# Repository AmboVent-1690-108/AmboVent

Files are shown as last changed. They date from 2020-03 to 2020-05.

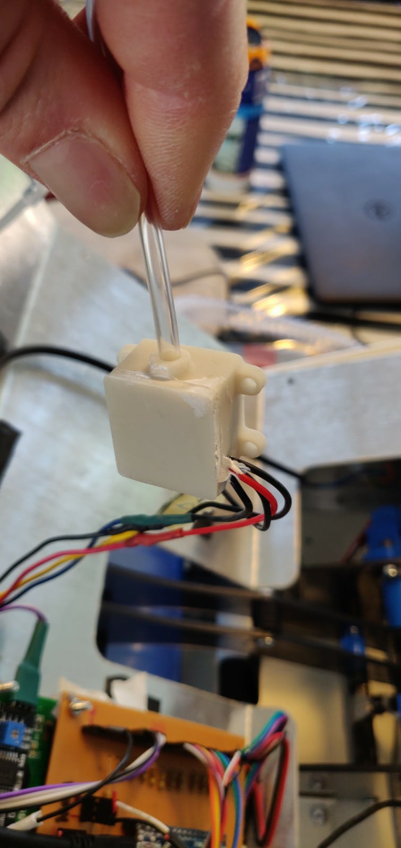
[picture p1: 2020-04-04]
Pressure Sensor/Pictures/WhatsApp Image 2020-04-04 at 16.27.53 (1).jpeg

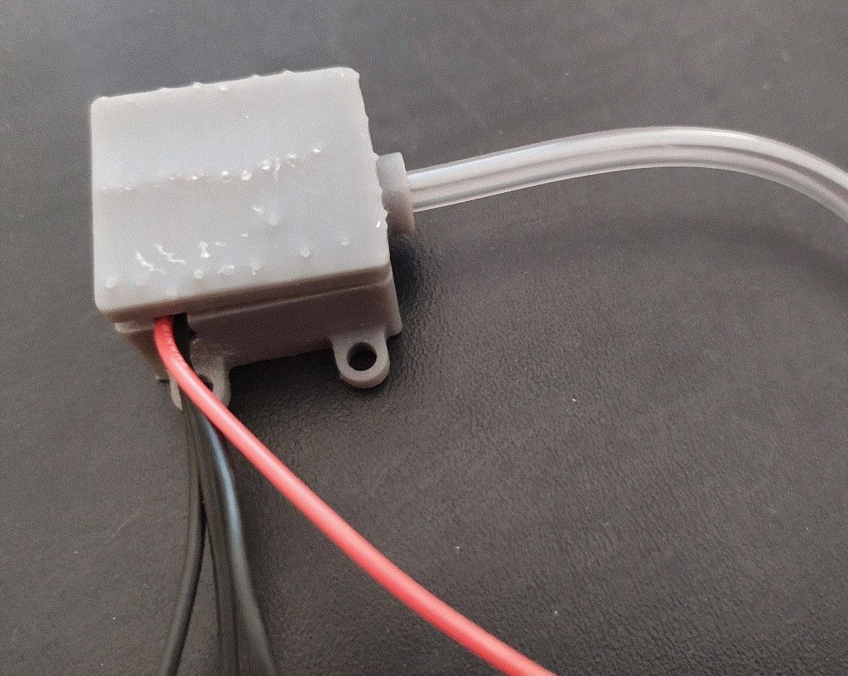
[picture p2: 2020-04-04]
Pressure Sensor/Pictures/WhatsApp Image 2020-04-04 at 16.28.07.jpeg

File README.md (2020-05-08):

# AmboVent  1690.108

    Automatic, Controlled Resuscitator Device
    Emergency ventilation alternative system
    Global Partnership for the Greater good
    Leading Open Source Code Mentality Initiative

## Emergency ventilation initiative coming out of Israel

## The device was not tested yet for its performance or safety; it is NOT approved for clinical use

### Who is behind it?  
**Lead by the CTO & innovation leader of the Israeli Air-Force 108 Electronic Depot and backed by a large community of innovators behind him, to include:**

1. 40 Professional Volunteers
1. Magen David Adom (Israel’s national EMS)
1. Physicians from leading Israeli hospitals such as Tel Aviv Sourasky and Hadassah JLM as well as other medical centers, Engineers, FIRST Israel mentors and students
1. The Haifa Technological Center Rafael
1. Israel Aerospace Industries
1. IAF Unit 108
1. The garage program by Microsoft Israel
1. IDC Herzeliya
1. and others...

## Developer Chat on Gitter:



## [AmboVent Website](https://1nn0v8ter.rocks/AmboVent-1690-108)

## [BOM list](https://docs.google.com/spreadsheets/d/1yqxRhruZpR-hO4cpbX6UkSeXTlXk1JLd_4aYDwuWj4k/edit?usp=sharing)

# AmboVent's Standard Copyright and Disclaimer Notice:

*Copyright ©2020. THE AMBOVENT GROUP FROM ISRAEL herby declares:  No Rights Reserved. Anyone in the world have Permission to use, copy, modify, and distribute this software and its documentation for educational, research, for profit, business and not-for-profit purposes, without fee and without a signed licensing agreement, all is hereby granted, provided that the intention of the user is to use this code and documentation to save human lives  anywhere in the world. For any question, contact dreliram@gmail.com.*

***IN NO EVENT SHALL THE AMBOVENT GROUP FROM ISRAEL, BE LIABLE TO ANY PARTY FOR DIRECT, INDIRECT, SPECIAL, INCIDENTAL, OR CONSEQUENTIAL DAMAGES, INCLUDING LOST PROFITS, ARISING OUT OF THE USE OF THESE SPECS, LIST OF MATERIALS, ELECTRONIC DESIGNS , SOFTWARE CODE AND ANY DOCUMENTATION, EVEN IF THE AMBOVENT GROUP FROM ISRAEL HAS BEEN ADVISED OF THE POSSIBILITY OF SUCH DAMAGE.
THE AMBOVENT GROUP FROM ISRAEL DISCLAIMS ANY WARRANTIES, INCLUDING, BUT NOT LIMITED TO, THE IMPLIED WARRANTIES OF MERCHANTABILITY AND FITNESS FOR A PARTICULAR PURPOSE. THE SOFTWARE AND ACCOMPANYING DOCUMENTATION, SPECS, LIST OF MATERIALS, ELECTRONIC DESIGNS, SOFTWARE CODE AND ANY DOCUMENTATION IF PROVIDED HEREUNDER IS PROVIDED "AS IS". THE AMBOVENT GROUP FROM ISRAEL HAS NO CLAIM THAT IT IS COMPLETED OR FUNCTIONAL AND HAS NO OBLIGATION TO PROVIDE MAINTENANCE, SUPPORT, UPDATES, ENHANCEMENTS, OR MODIFICATIONS.***

# Setup

## Software

1. (Required to build the code): [Arduino IDE](https://www.arduino.cc/en/Main/Software)
1. (Optional: recommended to edit the code): Eclipse project for Arduino source code _editing_ (NOT building):
    1. A general setup PDF guide can be found in the [eRCaGuy_dotfiles](https://github.com/ElectricRCAircraftGuy/eRCaGuy_dotfiles) project [here](https://github.com/ElectricRCAircraftGuy/eRCaGuy_dotfiles/blob/master/eclipse/Eclipse%20setup%20instructions%20on%20a%20new%20Linux%20(or%20other%20OS)%20computer.pdf). See also:
    1. [3-Software/Arduino/readme.md](3-Software/Arduino/readme.md).
    1. [3-Software/Arduino/arduino_core/readme.md](3-Software/Arduino/arduino_core/readme.md)
    1. [3-Software/Arduino/.clang-format](3-Software/Arduino/.clang-format) - there are some nice descriptions & info in here on Eclipse & Sublime Text 3 editors, as well as setting your Arduino IDE to use 4 spaces instead of 2 for tabs.
1. (Required to get a pull request accepted which modifies the code): `clang-format` automatic code format tool. Please run this on any PR (GitHub Pull Request) before submitting a PR!
    1. Linux (tested--works): 
        1. Install: 

                # Install it:
                sudo apt update
                sudo apt install clang-format

                # Ensure you have version 6 (the default for Ubuntu 18), for compatibility with 
                # the .clang-format file we are using; sample output: 
                # `clang-format version 6.0.0-1ubuntu2 (tags/RELEASE_600/final)`
                clang-format --version
        
        1. Use it: 
            1. Commit your changes so everything is backed up.
            1. Then run the clang formatter:

                    ./run_clang-format.sh

            1. Then review and commit these changes, if any.
            1. Now do a Pull Request.

    1. Windows:
        1. Install:
            1. Download and install [Git for Windows](https://git-scm.com/download/win)
            1. Download and install LLVM (which includes `clang-format`) version **6.0.1** (for compatibility--see above) [for Windows, here](https://releases.llvm.org/download.html). Here's a [direct link](https://releases.llvm.org/6.0.1/LLVM-6.0.1-win64.exe) if you like for the 64-bit version.
        1. Use it:
            1. Using the git bash terminal that comes with git for Windows, run the script:

                    ./run_clang-format.sh

            1. Make sure to do this before making any Pull Request (see Linux "Use it" instructions just above as well).

# Software Changelog
- Newest on top
- Follows Semantic Versioning: MAJOR.MINOR.PATCH; see: https://semver.org/ for rules & FAQ.
- The 6 most common recommended types of changes are (see here: https://keepachangelog.com/en/1.0.0/): Added, Changed, Deprecated, Removed, Fixed, Security

INITIAL DEVELOPMENT PHASE:
- Use version numbers 0.MINOR.PATCH for the initial development phase; ex: 0.1.0, 0.2.0, etc.
- Increment just the MINOR version number for each new 0.y.z development phase enhancement, until the project is mature enough that you choose to move to a 1.0.0 release
- You may increment the PATCH number for bug fixes to your development code, or just increment the MINOR version number if there are also enhancements

MORE MATURE PHASE:
- As the project matures, release a 1.0.0 version
- Once you release a 1.0.0 version, do the following (copied from semver.org):
- Given a version number MAJOR.MINOR.PATCH, increment the:  
1. MAJOR version when you make incompatible API changes,  
2. MINOR version when you add functionality in a backwards compatible manner, and  
3. PATCH version when you make backwards compatible bug fixes.  

## [v0.1.0] - 2020-04-22
- Added: changelog and started tracking a software "version" number via the changelog
- Fixed: continued incremental improvements of the software formatting and style: ex: moved global variables to their own lines

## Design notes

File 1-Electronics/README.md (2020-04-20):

AmboVent Electronic Design
--------------------------
## This directory contains the files needed to produce and/or change the electronic control board of AmboVent.

### The controller consist of a single PCB, with Arduino Nano mounted on it and a few other components. The board contains header connectors for varios system components:
- Front panel controls (pushbuttons, potentiometers, LEDs)
- Power input
- PWM control to the main motor
- Arm location feedback (potentiometer)
- I2C pressure sensor
 
All connectors have 0.1" spacing, and can accept either male or female headers. The power
input connector has 5mm spacing and it is designed for screw terminal connector type, but
direct wire connection is also feasible.

The PCB is designed with single layer, quick CNC fabrication in mind. It can be milled
with 1/32 mill. In this case, assembly will require a few wire bridges. If traditional, 
two layer fabrication method is used, a top layer can be used in place of the wire bridges.

#### SW1 – D2 - test button (used to initiate calibration)
#### SW2 – D4 - toggle breath on/off
#### SW3 – D5 - reset alarm button
#### Pot 1 – A2 – sets the range of motion as percentage from full range as set in calibration
#### Pot 2 – A3 – sets the respiration rate from 6 to 24 per minute
#### Pot 3 – A6 – sets the inspirium pressure from 30 to 70 cm H2O
#### J3 – connects to the position sensor potentiometer in the arm
#### J4 – connects to the motor controller PWM input (usually don’t connect the 5V)
#### J5 – connector to pressure sensor – if you use a 3.3V pressure sensor – supply 3.3V from the Arduino instead of the 5V

**Assemble the potentiometer for arm position sense such that when the arm moves down (presses the
Ambu more) – the voltage goes up. Range 0-5 volts
Assemble the user interface potentiometers such that during clockwise motion the voltage goes up.
Range 0-5 volts
Motor polarity shall be set such that PWM>50% to the controller results in the arm pressing the Ambu
(moving down).
The SW calibration procedure enable easy verification of the motor and position feedback polarity
(see calibration video for details)**

_Please note that the current sensor is **NOT** needed if you are using pressure sensor, it's possible to use it to monitor and limit the motor current while using the pressure sensor but again, not mandatory._

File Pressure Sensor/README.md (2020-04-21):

## General comments on the pressure sensor

_Please note that this sensor requires VDD of 3.3V and pull up to signal on the **SAME** VDD input, so using the current board schem could **damage** the sensor_

# Presure sensor and board
---------------------------------

We used the "SparkFun Pressure Sensor Breakout - MS5803-14BA"
The item can be found at the following link for $60US:
https://www.sparkfun.com/products/12909
It also can be found at other suppliers usually for the same price.

It is based of the TE MS5803-14BA sensor which can be bought
separately for cheaper price but usually in quantities of hundreds.
https://www.futureelectronics.com/p/analog--sensors--pressure/ms580314ba01-00-te-sensor-solutions-5058846
https://www.mouser.com/ProductDetail/Measurement-Specialties/MS580314BA01-00?qs=sGAEpiMZZMueJGT%2F0PGc4wvItXGMkWfD%252B0JwHIbyHlk%3D
If one uses the basic TE sensor a board should be designed with
few capacitors and resistors.

In case one want to use a different pressure sensor, we
recommend the following:
1. Pressure range is 100mbar (100cm H2O)
2. Digital communication - I2C preferred (analog communication 
will require high frequency averaging)

In case one prefer to use differential pressure sensor it will
improve reliability but will require a slightly change in the
arduino code.

Presure sensor box
---------------------------------

The box and cover are made from liquid ABS, using SLA technology
with resolution 0.05 to allow sealed box.

It is recommended to use flexible silicone wires to reduce stress
when mounting the pressure sensor in the box. 

Use a sealing silicone on the wires and around the box cover to
ensure complete sealed box

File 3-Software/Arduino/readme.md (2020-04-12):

## Description of files & folders:

## Main folders:
1. arduino_core = contains a symbolic link called "arduino" to the arduino installation directory so that your Eclipse project, for instance, can index it and allow you to jump to it while exploring the code
2. Libraries = required Arduino libraries you need to build this project
3. ventilation_machine = the main source code for this project

## Other files & folders:
1. .settings = Eclipse folder for this project
2. .cproject = Eclipse project file
3. .project = Eclipse project file
4. readme.md = this file

**Note that if you're new to Eclipse, a general setup PDF guide can be found in the [eRCaGuy_dotfiles](https://github.com/ElectricRCAircraftGuy/eRCaGuy_dotfiles) project [here](https://github.com/ElectricRCAircraftGuy/eRCaGuy_dotfiles/blob/master/eclipse/Eclipse%20setup%20instructions%20on%20a%20new%20Linux%20(or%20other%20OS)%20computer.pdf).**

When setting up an Eclipse project for Arduino, just set it up as a C/C++ project, then tell Eclipse that `*.ino` files are a type of C++ Source File (so that it will index them and open them up in its C/C++ editor with proper syntax highlighting) by following these instructions here: https://stackoverflow.com/questions/33474629/is-ecplise-cdts-indexer-limited-to-the-common-filetypes-for-sources-and-headers/33520998#33520998. In short: Window --> Preferences --> C/C++ --> File Types --> click "New..." --> type in "*.ino" as the pattern, and set the "Type" to "C++ Source File" --> click "OK" --> "Apply and Close". Eclipse will now automatically re-index the whole project, indexing all *.ino files as C++ source files! *These instructions have now been added to my Eclipse PDF doc above!*

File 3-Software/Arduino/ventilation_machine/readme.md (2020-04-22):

## Build size notes:
(Newest on TOP; date format is YYYYMMDD)

---

20200422-0136hrs (git hash 222e6966211a877936bd2962692c0c57bd665e2f; branch more_incremental_improvements) (IDE 1.8.12) (Arduino Nano)  
Note: memory usage went up because we are now storing and printing the version number at startup.

    Sketch uses 18318 bytes (56%) of program storage space. Maximum is 32256 bytes.
    Global variables use 1074 bytes (52%) of dynamic memory, leaving 974 bytes for local variables. Maximum is 2048 bytes.

---

20200420-0049hrs (git hash 493985f; branch fix_formatting) (IDE 1.8.12) (Arduino Nano) - PR #46: https://github.com/AmboVent-1690-108/AmboVent/pull/46

    Sketch uses 18176 bytes (56%) of program storage space. Maximum is 32256 bytes.
    Global variables use 1046 bytes (51%) of dynamic memory, leaving 1002 bytes for local variables. Maximum is 2048 bytes.

---

20200419-2312hrs (git hash 078871e05ddd5890747f49222d46a7b30fd7b023; branch master) (IDE 1.8.12) (Arduino Nano) - no changes made yet to the code:

    Sketch uses 18174 bytes (56%) of program storage space. Maximum is 32256 bytes.
    Global variables use 1046 bytes (51%) of dynamic memory, leaving 1002 bytes for local variables. Maximum is 2048 bytes.

---

20200411-2217hrs (IDE 1.8.8) (Arduino Nano) - no changes made yet to the code:

    Sketch uses 18280 bytes (59%) of program storage space. Maximum is 30720 bytes.
    Global variables use 1882 bytes (91%) of dynamic memory, leaving 166 bytes for local variables. Maximum is 2048 bytes.
    Low memory available, stability problems may occur.

---

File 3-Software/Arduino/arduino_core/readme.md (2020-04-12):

Inside this folder should be a symbolic link to your arduino installation folder. This way, an Eclipse project, for instance, can have full access to all of the Arduino source code to allow jumping to the core implementations of Arduino functions and definitions while exploring the code. 

## References:
1. How to make symbolic links in Windows: 
   https://www.howtogeek.com/howto/16226/complete-guide-to-symbolic-links-symlinks-on-windows-or-linux/

## How to make the symbolic link to the core Arduino source code:

**1) To create a symbolic link on Mac or Linux**, the command looks like this. This will create a symbolic link folder called "arduino" right here: 

    ln -s "/path/to/arduino_installation_folder" arduino

Example: 

    cd /path/to/here
    ln -s "/home/gabriel/Downloads/Install_files/Arduino/arduino-1.8.8" arduino

**2) To create a symbolic link on Windows**, the command looks like this:

    mklink /D arduino "C:\Users\gabriel\Downloads\Install_files\Arduino\arduino-1.8.8"

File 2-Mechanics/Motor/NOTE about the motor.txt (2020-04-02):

We used the am-2235a Snow Blower Motor With Hex Shaft

Any equivalent motor can fit, with a relevant adapter.
- 12V
- RPM 70 to 100
- Torque >7NM

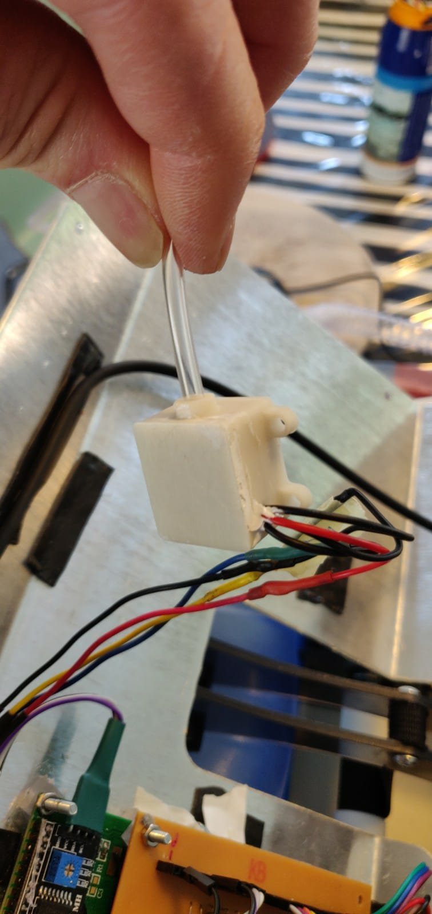
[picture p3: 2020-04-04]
Pressure Sensor/Pictures/WhatsApp Image 2020-04-04 at 16.27.52 - Copy.jpeg

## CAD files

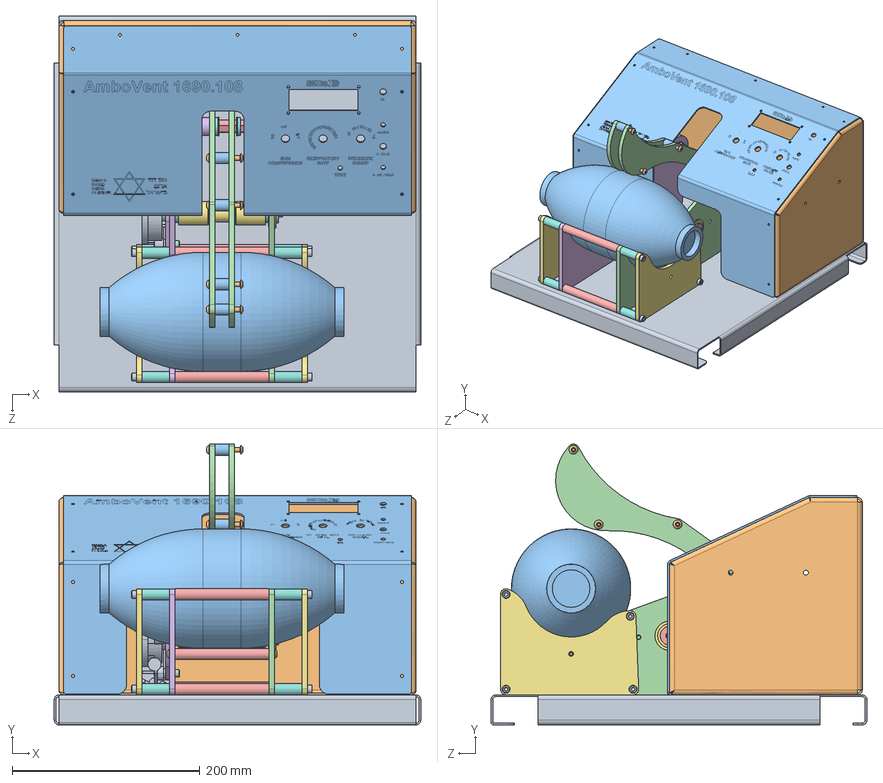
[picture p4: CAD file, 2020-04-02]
2-Mechanics/Casing/AMBOVENT.SLDASM
390.0 x 298.8 x 400.0 mm
AMBOVENT-1-1
AMBOVENT-1-2
AMBOVENT-1-3-1
socket head cap screw_am x 10
socket button head cap screw_am x 14
0.5in Hex 1.125in OD 217-3875 Flanged Bearing x 3
E-clip 0.5in shaft x 2
Ambu Air Tank
EMS22Q51-B28-LS4 Digikey EMS22Q51-B28-LS4-ND
am-2235a SnowBlower with Hex Shaft
socket head cap screw_ai x 4
flat washer wide_am
prevailing torque hex nut_am x 2

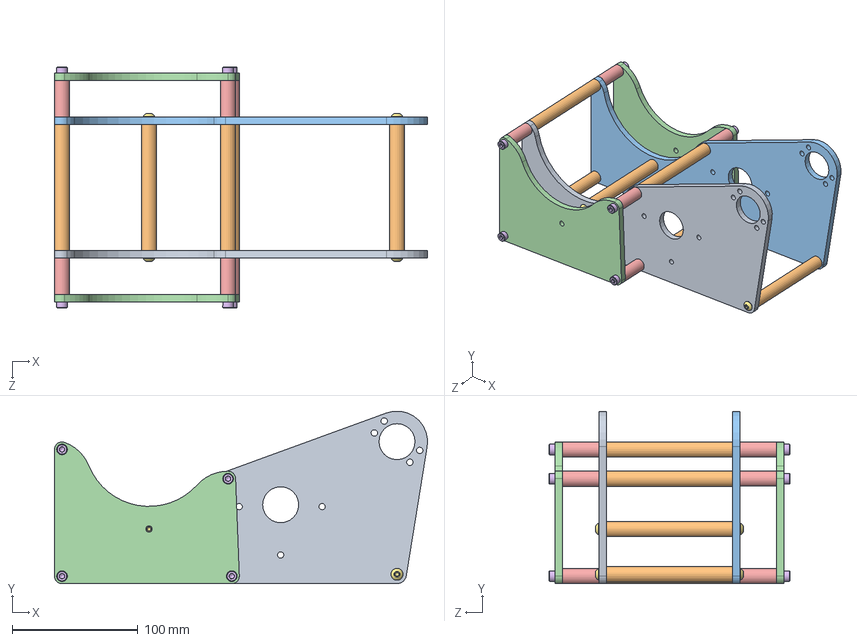
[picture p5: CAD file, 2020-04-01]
2-Mechanics/Mechanism/SolidWorks Pack and Go/1690-20-8320.SLDASM
296.9 x 137.2 x 192.0 mm
socket head cap screw_am x 8
socket button head cap screw_am x 4

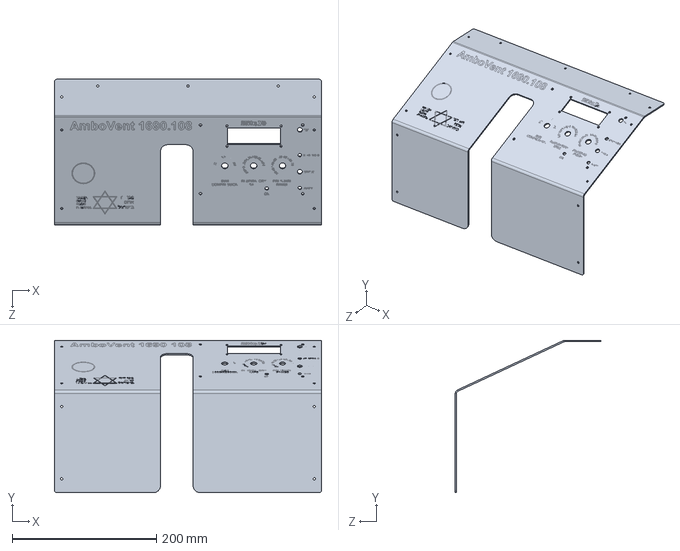
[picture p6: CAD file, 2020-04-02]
2-Mechanics/Casing/AMBOVENT-1-3.SLDASM
370.0 x 211.2 x 201.7 mm

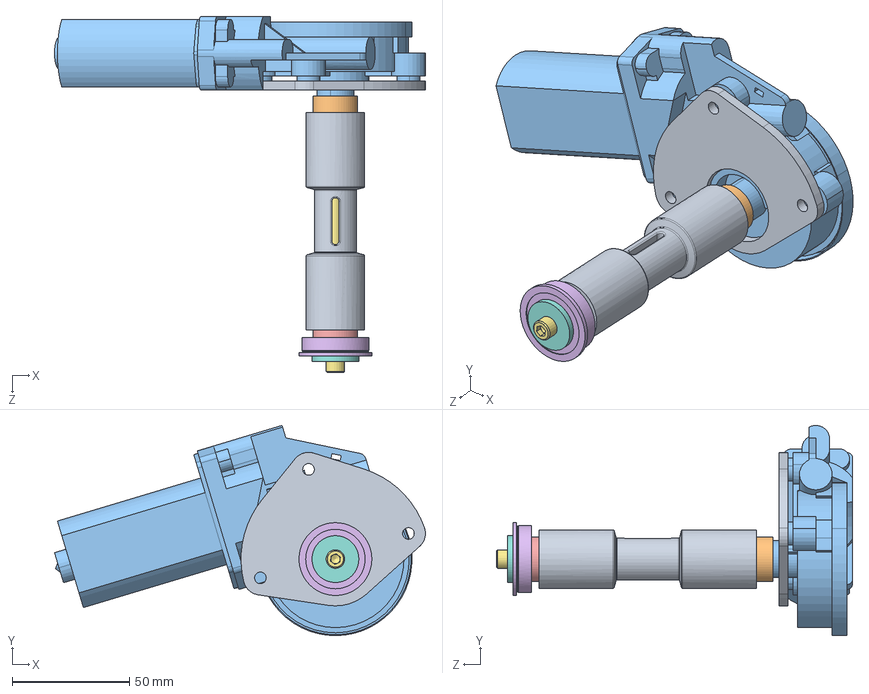
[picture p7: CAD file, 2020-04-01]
2-Mechanics/Mechanism/SolidWorks Pack and Go/1690-20-8390.SLDASM
158.5 x 89.8 x 152.2 mm
am-2235a SnowBlower with Hex Shaft
0.5in Hex 1.125in OD 217-3875 Flanged Bearing
socket head cap screw_ai
flat washer wide_am

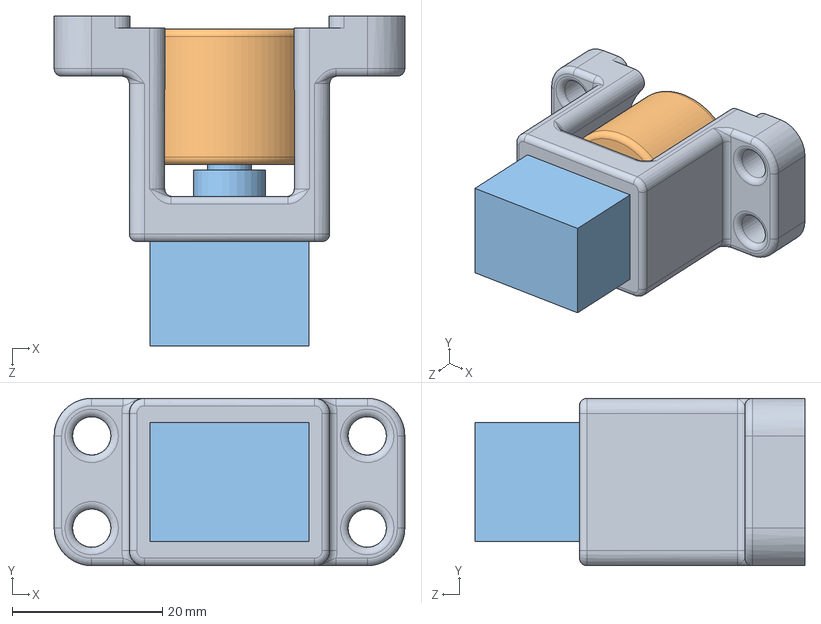
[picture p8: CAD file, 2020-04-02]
2-Mechanics/Casing/1690-20-8340.SLDASM
46.7 x 22.3 x 43.9 mm
EMS22Q51-B28-LS4 Digikey EMS22Q51-B28-LS4-ND

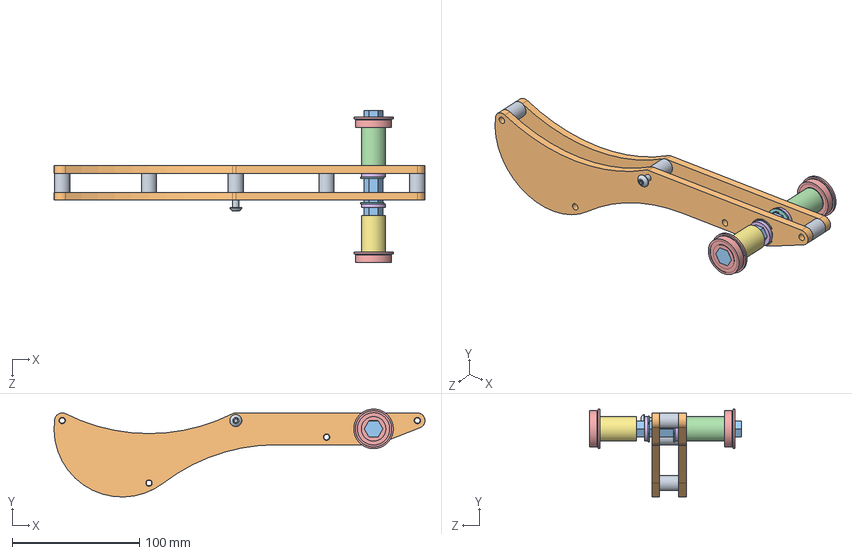
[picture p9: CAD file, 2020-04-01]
2-Mechanics/Mechanism/SolidWorks Pack and Go/1690-20-8310.SLDASM
291.3 x 69.0 x 119.0 mm
0.5in Hex 1.125in OD 217-3875 Flanged Bearing x 2
E-clip 0.5in shaft x 2

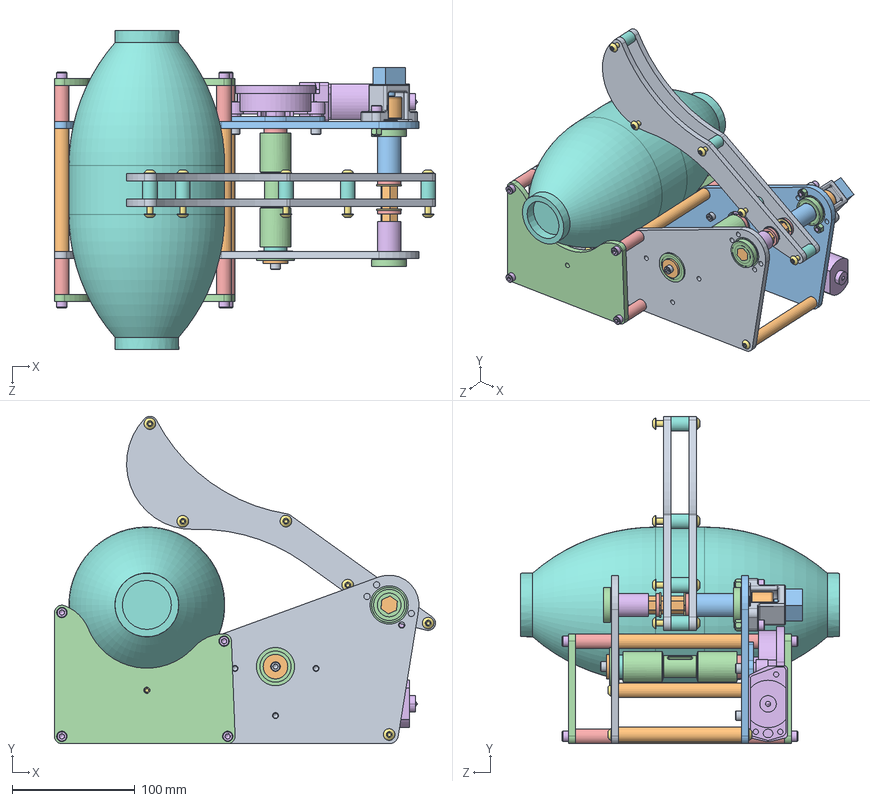
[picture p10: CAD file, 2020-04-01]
2-Mechanics/Mechanism/SolidWorks Pack and Go/1690-20-8300.SLDASM
310.4 x 266.8 x 260.0 mm
socket head cap screw_am x 10
socket button head cap screw_am x 14
0.5in Hex 1.125in OD 217-3875 Flanged Bearing x 3
E-clip 0.5in shaft x 2
Ambu Air Tank
EMS22Q51-B28-LS4 Digikey EMS22Q51-B28-LS4-ND
am-2235a SnowBlower with Hex Shaft
socket head cap screw_ai x 4
flat washer wide_am
prevailing torque hex nut_am x 2

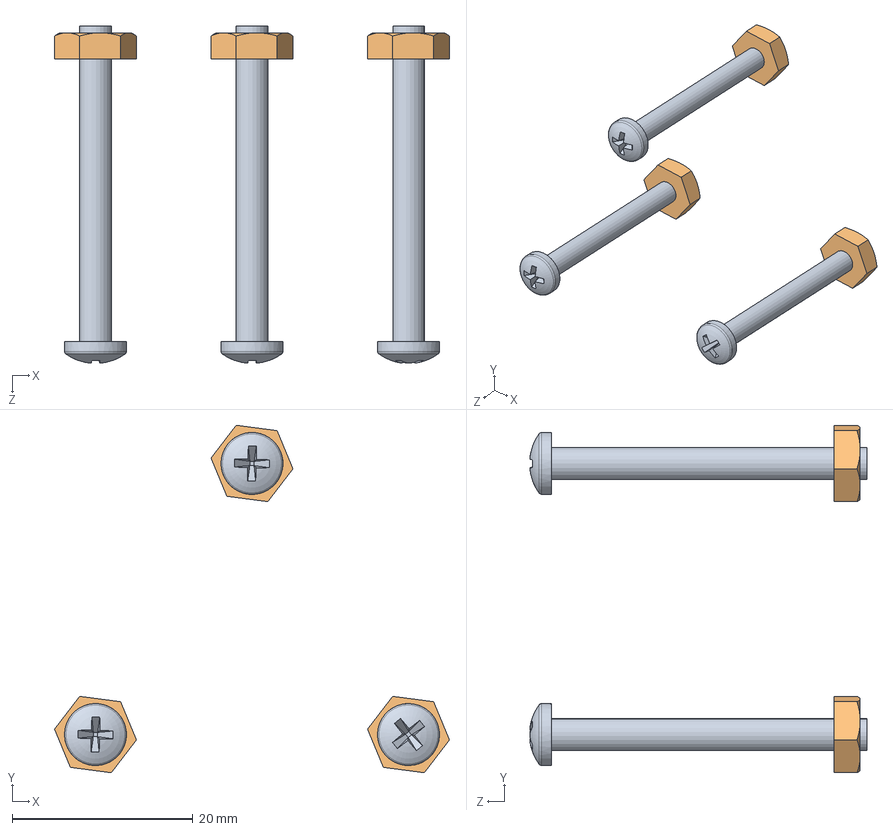
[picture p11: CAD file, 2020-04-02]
2-Mechanics/Casing/AMBOVENT-2-3.SLDASM
43.7 x 38.5 x 37.3 mm
pan cross head_ai2 x 3
machine screw nut hex_ai x 3

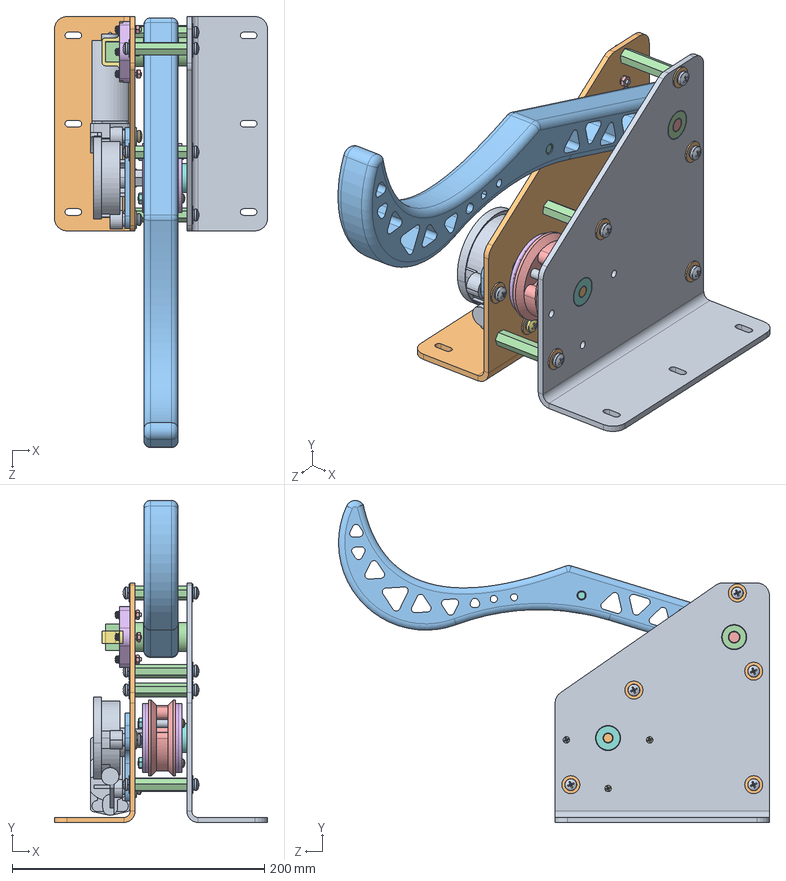
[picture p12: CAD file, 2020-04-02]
2-Mechanics/Casing/AMBOVENT-2.SLDASM
169.0 x 255.4 x 341.7 mm
AMBOVENT-2-1
AMBOVENT-2-2
AMBOVENT-2-12
AMBOVENT-2-11 x 2
AMBOVENT-2-3-1
AMBOVENT-2-3-2 x 4
pan cross head_ai2 x 5
machine screw nut hex_ai x 3
AMBOVENT-2-3-3
AMBOVENT-2-4
AMBOVENT-2-6
encoder
AMBOVENT-2-7
AMBOVENT-2-8
AMBOVENT-2-9
AMBOVENT-2-5
pan cross head_ai x 15
flat washer type b regular_ai x 13
lock washer spring regular_ai x 13
AMBOVENT-2-10 x 5
hex nuts_35649_mil x 4
split lock_mil x 4
flat washer type b narrow_ai x 8
straight pin_ai
am-2235a SnowBlower with Hex Shaft

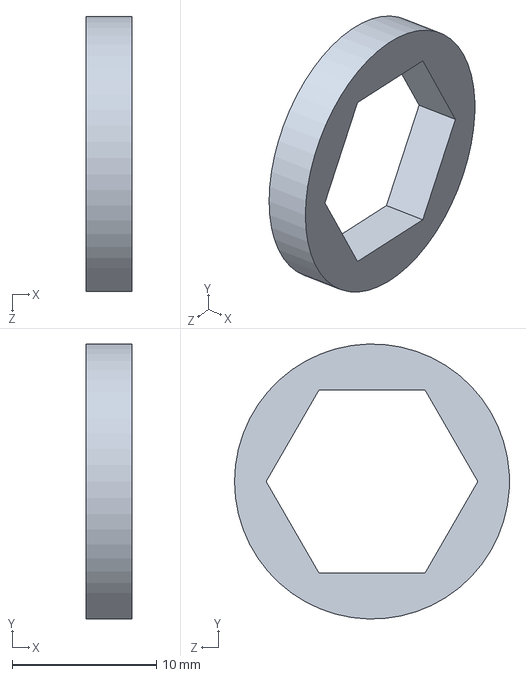
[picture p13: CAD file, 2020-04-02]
2-Mechanics/Casing/1690-20-8394.SLDPRT
3.19 x 19.0 x 19.1 mm

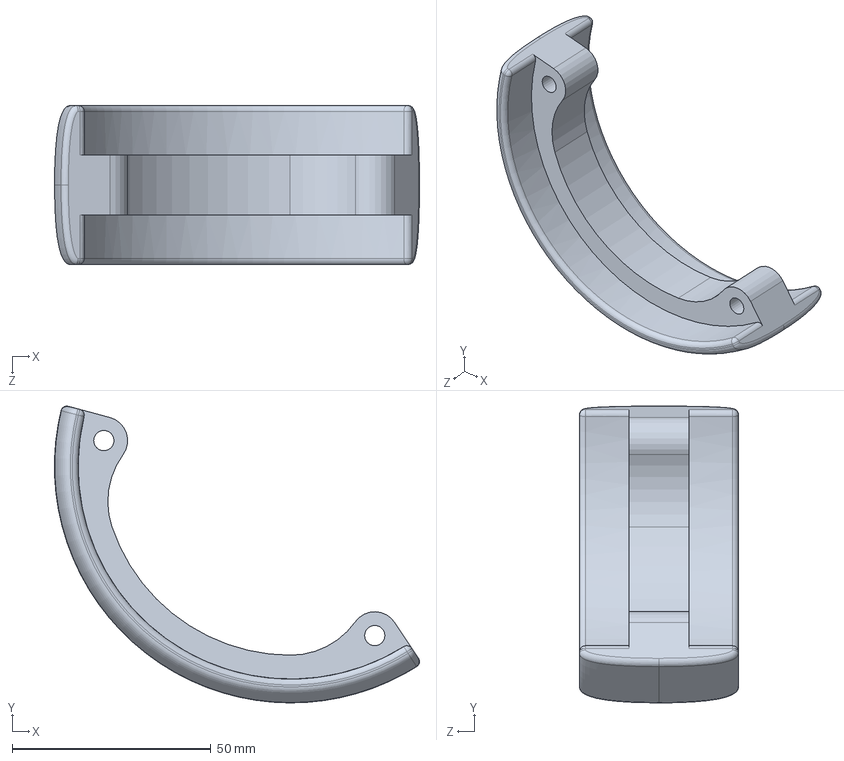
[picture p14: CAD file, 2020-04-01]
2-Mechanics/Mechanism/Ambu protection print/1690-20-8319.SLDPRT
91.8 x 74.7 x 40.0 mm

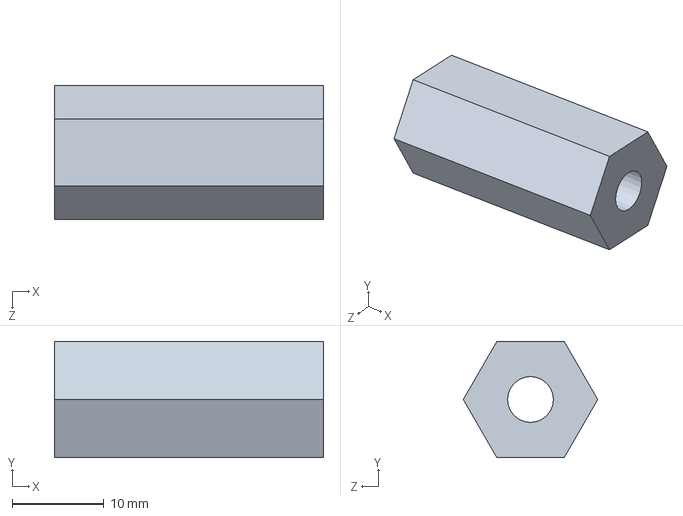
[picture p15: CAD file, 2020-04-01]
2-Mechanics/Mechanism/SolidWorks Pack and Go/1690-20-8393.SLDPRT
29.3 x 12.7 x 14.7 mm

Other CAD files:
2-Mechanics/Casing/1690-20-8310.SLDASM
2-Mechanics/Mechanism/SolidWorks Pack and Go/1690-20-8340.SLDASM
2-Mechanics/Casing/1690-20-8320.SLDASM
2-Mechanics/Casing/1690-20-8390.SLDASM
2-Mechanics/Casing/1690-20-8300.SLDASM
2-Mechanics/Mechanism/Assembly in other formats/1690-20-8300 REV7 26.3.2020 20_30.STEP
2-Mechanics/Casing/0.5in Hex 1.125in OD 217-3875 Flanged Bearing.SLDPRT
2-Mechanics/Casing/1690-20-8311.SLDPRT
2-Mechanics/Casing/1690-20-8313.SLDPRT
2-Mechanics/Casing/1690-20-8314.SLDPRT
2-Mechanics/Casing/1690-20-8315.SLDPRT
2-Mechanics/Casing/1690-20-8316.SLDPRT
2-Mechanics/Casing/1690-20-8317.SLDPRT
2-Mechanics/Casing/1690-20-8321.SLDPRT
2-Mechanics/Casing/1690-20-8322.SLDPRT
2-Mechanics/Casing/1690-20-8323.SLDPRT
2-Mechanics/Casing/1690-20-8325.SLDPRT
2-Mechanics/Casing/1690-20-8326.SLDPRT
2-Mechanics/Casing/1690-20-8341.SLDPRT
2-Mechanics/Casing/1690-20-8342.SLDPRT
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

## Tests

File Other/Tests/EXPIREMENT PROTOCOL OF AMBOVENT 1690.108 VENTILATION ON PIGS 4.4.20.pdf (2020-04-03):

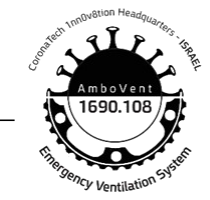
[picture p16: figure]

### Experiment Protocol - Ventilation on Pigs

בלמ"ס 1

## EXPIREMENT PROTOCOL OF AMBOVENT 1690.108 VENTILATION ON PIGS

### ABSTRACT

On 2020 the COVID-19 pandemic outbreak occurred and infected a major papulation section, mainly the elderly.
Most of the hard-conditioned patients end up ventilated due to the virus that attack the lung.
MDA, First team and the army gathered for an enterprise called "AMBOVENT 1690.108" to utilize the standard Ambo bags and transformed it to an open-source, low-budget ventilation device that any country can use and mass product for their hospitals use.

To determine the safety and efficacy of the AMBOVENT 1690.108 a pre-clinical trial on live

animal model is planned.

A 50 Kg domestic pig was chosen as the animal model due to its similarity in anatomy

and physiology to the human body.

The pig will be acclimates in the Large animal Care Unit of the Hebrew University

following transfer from Lahav. Fasting will be initiated on the night prior to the study

with free access to water. On the day of the study pre-medication of IM Ketamine and

IM Xylazyne will be given and then IV access will be established. Orotracheal

intubation will be performed following induction with propofol and maintenance of

general anesthesia will be achieved with propofol drip 1% 0.02-0.2 mg/kg/min

throughout the study.

Ventilation will be first achieved with a standard ventilator for 15 minutes. Machine

parameters and physiologic parameters will be documented continuously and blood

gases will be drawn.

The Ambovent will be attached for 10 minutes and ambovent parameters and

physiologic parameters will be documented continuously and blood gases will be

drawn.

The ambovent parameters will be changed every 10 minutes to increase/decrease tidal

volume/respiratory rate and pressure and the Ambovent parameters will be compared

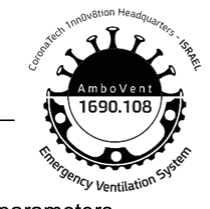
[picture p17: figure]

### Experiment Protocol - Ventilation on Pigs

בלמ"ס 2

to the true parameters using a standard ventilation machine. Physiologic parameters

will be documented continuously and blood gases will be drawn.

Any Adverse Events or malfunctions of the Ambovent will be recorded.

In case of pneumothorax, a chest drain will be inserted and the study will be continued

if possible.

Parameters that will be documented will be:

Overall time of ventilation

Ambovent parameters: FiO2, PEEP, Volume, Resp Rate, Pressure

True parameters: Tidal volume, Ventilation rate, PIP, P mean

Physiologic parameters: O2 Sat%, HR, BP, ETCO2

Blood gases: PH, aO2, aCO2, HCO3

Following the study, euthanasia will be done using IV KCl.

Hour

min | FiO2 | PEEP | Volume | V rate | Pressure | TV | V rate | P max | P mean | O2 Sat | HR | a BP | ETCO2 | PH | aO2 | aCO2 | aHCO3
Ambovent parameters | True parameters | Physiologic parameters | Blood gases

AE/ Comments

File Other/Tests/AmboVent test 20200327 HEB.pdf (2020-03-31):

- 1 -

27/03/2020
לכבוד:
הנדון: פרויקט אמבוטומטי – דוח ניסוי מדידות ראשון

.1 היום בוצעה בדיקת מערכת אמבוטומטי V2( עם חוט משיכה( .2 הבדיקה בוצעה בחברת פלקס על צב"ד אנלוגי של מכשירי הנשמה. א. לצב"ד יש ריאה מכנית מלאכותית שמציגה נפח ניפוח על סקאלה אנלוגית. ב. לצב"ד יש שעון לחץ אנלוגי שמודד הלחץ בתוך הריאה. .3 עיקרי הבדיקות שבוצעו:
א. מדידה השוואתית של לחץ אנלוגי מול הלחץ הנמדד בחיישן שלנו. ב. מדידת אורך הלחיצה על ה"אמבו" לעומת נפח הנשיפה הנמדד. .4 הסט אפ שנבדק
א. אמבוטומטי דגם .2 )עם חוט( שמאפשר לחיצה עמוקה. ב. אמבו כחול, ירוק ודו שכבתי כחול ג. סנסור לחץ מחובר בין ווסת ה PEEP לריאה המלאכותית, ה PEEP כוון ל 10 mBar( הלחץ שנותר בריאות לאחר הנשיפה(
1( ככל שלחץ ה PEEP יותר גבוה )אפשר לכייל לפי הבריטים בין 5 – 25 mBar יותר קשה לאמבו להנשים.
ד. צינור בין האמבו לריאה כ 1 מטר אורך. .5 ממצאים:
א. לחץ PEEP כוון ל 10 mBar בכל הבדיקות, מדדנו 12 הקצה הנשיפה והייתה ירידה לכיוון ,6 הצב"ד מדד 12 וירידה לכיוון .9 בלחצים הנמוכים הללו זה סביר. ב. אמבו כחול שקוף, קצב 14 פעימות לדקה
| | נפח נמדד CC – צב"ד לחת שלנו mBar לחץ צב"ד mBar הערות
21 | 27 | 400
25 | 35 | 500
30 | 60 | 700
| | פחות מ 350 20 16 לייחוס לחצים
| | פחות מ 400 25 20 לייחוס לחצים
ג. אמבו כחול שקוף, קצב 24 פעימות לדקה
| | | נפח נמדד CC – צב"ד לחת שלנו mBar לחץ צב"ד mBar הערות
מגדילה את מהירות הזרימה בלחיצה ומעלה מעט הלחץ | | | 400 28 22 העלאת הקצב
| 26 | 40 | 500
| 32 | 60 | 700

- 2 -

ד. בדיקת השוואת נפח לחיצה למדידת הפוטנציומטר של הכננת: 1( נותר נפח בריאה המלכותית בזכות השסתום PEEP
| | פוטנציומטר )ערך אנלוגי( מדידת ריאה מלאכותית ב CC הערות
| | | | נמוך גבוה נמוך גבוה
| 300 | 100 | 725 | 275
| 400 | | 800
| 600 | | 950
בלחץ PEEP של 10 | | 1000 700 700 זה הכי הרבה שהצלחנו לסחוט

ה. בדיקת נפח מירבי לסחיטה מאמבו 1( אמבו כחול קטן דו שכבתי – 600 CC

2( אמבו ירוק שקוף 700 CC, לחץ צב"ד 35 mBar

3( אמבו כחול שקוף 700 CC, לחץ צב"ד 35 mBar

.6 תובנות ונושאים לטיפול
א. סנסור הלחץ דורש כיול ראשוני של לחץ ייחוס כי אינו דיפרנציאלי, בעת הכיול נדרש לוודא שאין עליו לחץ, כלומר הנצרת לא מחוברת למטופל. 1( אין לכייל עם מטופל או ריאה מדמה מחוברת. ב. אנחנו מודדים דיגיטלית והמדיד רפרנס שנבדק – אנלוגי – יתכן שיש כאן החלקה משמעותית של פיק הלחץ ויתכן שיש לנו צורך לכייל את המדידים 1( הנושא בבדיקה של אלון לוי. ג. גם הריאה המכנית מראה על סקלת סרגל אנלוגי )מתנפחת כמו גרמושקה( את נפח ההנשמה – לא בטוח שזה מדוייק מספיק.
ד. האמבו שונים זה מזה, בדגמי הסיליקון השקופים הצלחנו לסחוט 700CC בערך ומיצינו את המנוע לקצה. יתכן שממש הגענו לחומר על חומר למול בסיס האמבו ולכן המנוע התחמם. 1( האמבו מוגבל ביכולת התגובה שלו ללחיצה, הוא מתנגד ללחיצה. 2( בדקנו אפשרות להרחיב איזור הלחיצה מ כ 30 ל 60 מ"מ )בדיקה ידנית( האמבו מתקפל מידי ולוקח לו זמן להפתח
3( צריך ללחוץ עליו במרכז עם זרוע של 30 עד 40 מ"מ ולא לגרום לקריסה של האיזורים הקוניים שלו שצריכים להשאר שלמים כדי ליצור את הקפיציות לחזרה. 4( כתוצאה נראה שקצב ההתאוששות של האמבו לא יאפשר להגיע לקצבי הנשמה גבוהים מ 24 פעימות לדקה – מחייב המשך בדיקה מול צב"ד יותר מתקדם

- 3 -

ה. המנוע התחמם לאחר כחצי שעה של עבודה בסחיטה מלאה, שתי אפשרויות לסיבה: 1( סביר מאוד שבניסיון סחיטה הגענו לנעילה מכנית על ה אמבו כנגד עצמו ומתקן האחיזה – מצב זה ממש לא בריא ויש למנוע אותו בכיול המערכת, מעבר לעומס על המנוע יהיה נזק לאמבו.
2( המנוע היה "חלון" ישן דגם 2013 וכנראה "יבש" כי במדידה שגיורא עשה זרם הפתיחה והלחיצה דומים אז יתכן חיכוך גבוה במנגנון. א( גיורא בודק העמסה למשך כמה שעות מחר. 3( נבדוק אפשרות להוסיף "דריכה" בקפיץ לזרוע הלחיצה על מנת להקל על הלחיצה על חשבון ההרמה, במנוע חלזוני אין בעיה עם עצירה במקום ללא עומס. אבל זה יחייב להוסיף גלגל שיניים לזרוע מה שיסבך הפתרון המכני והייצורי – לא להגיע לשם.

.2 בברכה,
זאב שניאורסון

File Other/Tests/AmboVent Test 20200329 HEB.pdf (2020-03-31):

- 1 -

29/3/2020
לכבוד:
הנדון: פיתוח "אמבוטומטי" – ניסוי מול מערכת מדידה בבי"ח רמבם

.1 היום התקיימה בדיקה והצגת המכשיר ברמב"ם בהשתתפות: א. צוות אמבוטומטי – גיורא קורנבלאו, ד"ר גדעון מרירי, זאב שניאורסון ב. רמב"ם:
1( ד"ר אלי ויסמן סגן מנהל בית החולים רופא מרדים 2( ד"ר ירון בר לביא מנהל חטיבת טיפול נמרץ רמב"ם יו"ר האיגוד הישראלי לטיפול נמרץ 3( ג'ורג' דאוד טכנאי הנשמה 4( אלי ארבל טכנאי הנדסה רפואית 5( גינדי ספושניקו מהנדס מנהל הנדסה רפואית ג. בצהוב – נושאים להתייחסות, טיפול ושינוי .2 רקע טכני
א. מכשיר ההנשמה שפותח על ידי הצוות שלנו מבוסס אמבו, זרוע רובוטית לוחצת לסחיטת האמבו ומערכת בקרה
ב. פונקציות ההנשמה הנשלטות כיום על ידי בוררים פוטנציומטר 1( עומק לחיצה שמתורגם לנפח הנשמה וללחץ הנשמה עליון )תלוי דגם אמבו ומהירות הלחיצה( – נמדד על ידי פונטציומטר על ציר זרוע הלחיצה – המהלך ניתן לכיול פשוט לכל דגם אמבו. 2( קצב הנשמה לדקה 6-24 )כל 2( – מדידת זמן מבוקר תוכנה בלבד 3( לחץ התרעה PIP( 30-40:40-50:50-60:60-70 – )מבוסס סנסור לחץ מסחרי לתחום זה, לא דיפרנציאלי.
ג. מכשיר האמבו הרובוטי שפותח חש רק את לחצי מערכת האוויר ומסוגל לזהות עליית לחץ )כתוצאה מנשיפה עצמית של המטופל במהלך הנשמה למשל( ד. הצב"ד שהשתמשנו בו:

ה.

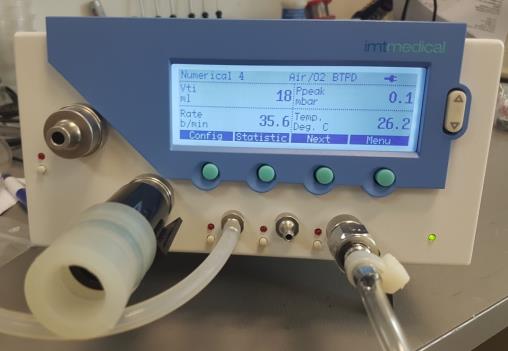
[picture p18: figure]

ו. הוא מודד
1( נפח הנשמה
2( לחץ הנשמה גבוה )PIP), לחץ שיורי PEEP

- 2 -

3( קצב הנשמה
ז. בוצע כיול בין אורך הלחיצה לנפח ההנשמה. ח. בוצע השוואה בין מדידת הלחץ בצב"ד לבין הלחץ שאנחנו מודדים – הסטיה ב PIP, PEEP הינה ±0.5 מיליבאר = המערכת שלנו נותנת המידע הנכון. 1( אם נחליף סנסור לחץ יש לבחון הנושא שנית .3 סט אפ המדידה
א. המחשב שייך להצגת פנל הבקרה של המכשיר שלנו, ב. המכשיר מדגם ה2.0 )עם כננת( לא בצורה הסופית )כננת 25 מ"מ, מנוע חלון 2013 ישן( אין תמיכות צד למניעת "בריחת" האמבו. – כל אלו לא משפיעים פונציונלית על הפעולה, במעבר למנוע וכננת סופי נדרש לבחון שוב שעומדים בקצבי העבודה הנדרשים מבחינת מהירות הסחיטה

ג.

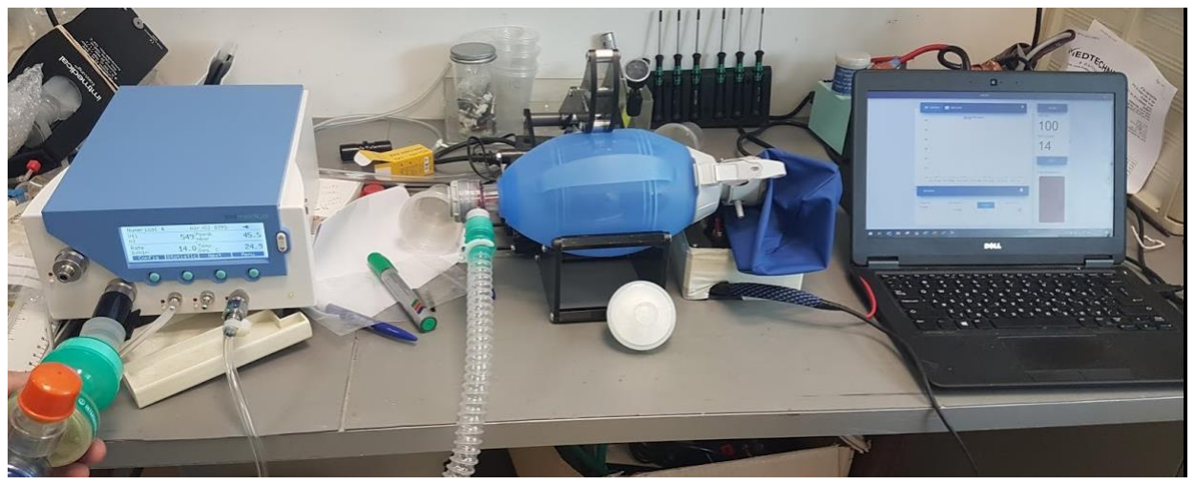
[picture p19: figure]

.4 מהלך הבדיקה תוצאות ותובנות: א. התברר שהמכשיר שלנו מסוגל להנשים מטופל בנפח של כ 550 סמ"ק ומטה, לחץ מירבי של 50 מיליבאר ומטה.
ב. פונקציות המערכת הקיימות ושיפורים נדרשים: 1( קביעת נפח הנשמה – מ 1/3 ועד 3/4 יבוצע בסקאלה רציפה, הרופא יקבע ערך זה לפי החלטתו כאשר המשוב שהוא יראה הינו נתון לחץ PIP( הלחץ המירבי בהנשמה(.

א( השינוי כאן הוא הפיכת הסקאלה לרציפה )לציין ,1/3 ,1/2 3/4 לייחוס בלבד(. 2( קביעת קצב הנשמה – מה שיש מתאים – סקאלה של 6 עד 24 )לא נדרש בפועל יותר מ 18( ג. לגבי שחרור בסוף הלחיצה, הבקשה של מנהל טיפול נמרץ ברמב"ם )והייתה הסכמה של טכנאי הנשמה ועוד אנשים שלהם( היא להשהות עוד במצב הלחוץ . לחכות לפני שחרור הלחץ )כדי לדחוף קצת את הנוזלים ולעזור לריאות לקבל את הנפח(. הפרוטוקול הקבוע שלהם הוא חצי שניה השהייה.. ובחולי קורונה הם לפעמים מגדילים עד שניה לפני שחרור 1( קביעת לחץ מירבי PIP לעצירת הנשמה ואזעקה – הסקאלה של היום ,30-40 ,40-50 ,50-60 60-70 –

ממליץ להחליט שהתחומים יהיו מדוייקים ללחץ PIP קבוע למשל: ,40 ,45 ,50 ,60 ,65 70 – זה יקל על המפעילים להבין מה זה עושה א( נתון לחץ זה קובע את הערך לעצירת ההנשמה עם מגיעים אליו בגלל שהמטופל נושף, בעייה בהנשמה, אחר.

- 3 -

ב( לבקשת הרופאים ברמב"ם שתואמה גם עם יובל ואריה סוכם שאם המערכת מגיעה ללחץ הPIP מבוצעת הפעולה הבאה:
)I )עצירת הלחיצה )ללא הרמת הזרוע( כדי לשמר לחץ בריאות עד לסיום מחזור ההנשמה )לחיצה ושימור(.
)II )המשך הנשמה כמתוכנן, אם הלחץ המירבי חוזר פעם שניה להשמיע אזעקה. 2( מחזור הנשמה נראה כך:
א( לחיצה על האמבו )לפי האורך הנקבע( בתוך כ 0.8 שניה – נתון קבוע ללא קשר לקצב ההנשמה. ב( השארת הזרוע למטה למשך 0.5 שניה - נתון קבוע ללא קשר לקצב ההנשמה – )זה מידע חדש וחשוב, הכלל הוא עצירת הלחץ בריאות למשך 0.5 שניה עד 0.9 שניה – סוכם עם הרופא בפגישה שנקבע 0.5 שניות קבוע(.
ג( הרמת הזרוע )מייד בהמרת הזרוע יורד הלחץ במערכת(. ד( המתנה לסוף מחזור ההנשמה )נניח בקצב של 15 הנשמות לדקה כל מחזור הוא 4 שניות(.
ד. סינכרון % הלחיצה על האמבו למול נפח ולחץ שנמדדו לדגם מקורי של AMBU מבוגרים

1( העליון – אמבו שהיה אצל גיורא 2( התחתון – אמבו )אוצו דגם, רק חדש יותר( שהיה בבית החולים )מרגיש יותר "קשה"( 3( ניתן לראות שבלחיצה מקסימלית )לפני ריקון מלא( הצלחנו לסחוט 620 מהאמבו הרך שהיה אצל גיורא ו 550 סמ"ק מהאמבו ה"קשה" של בית החולים 4( בעבודה ב 100% לחיצה בקצב של 24 פעימות לדקה המערכת עובדת קרוב לסף העבודה שלה ולא מומלץ להגיע לשם, לפי הרופאים מספיק 30-35 מיליבאר לחץ הנשמה מגביל ל 60% עד 75% לחיצה תלוי באיזה אמבו.

ה.

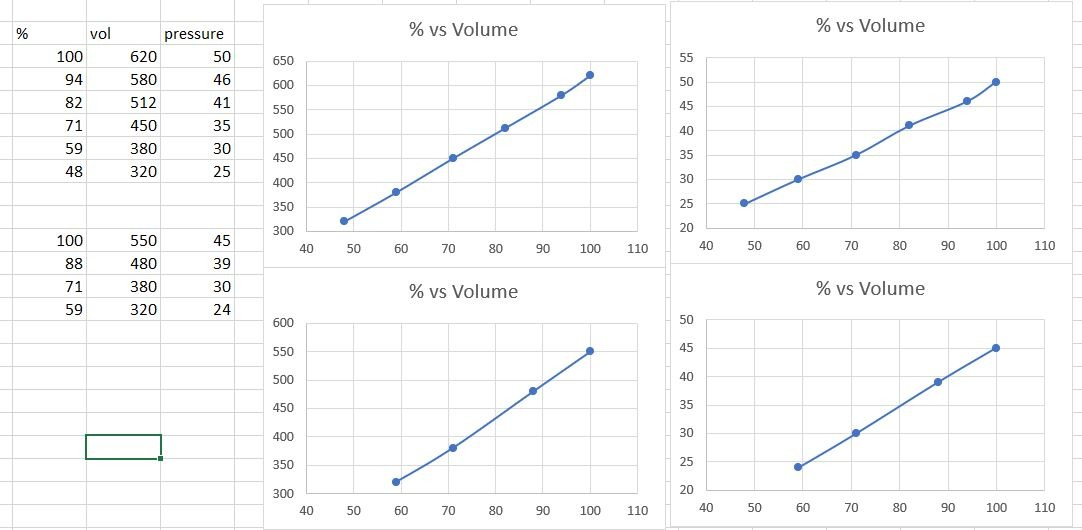
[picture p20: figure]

ו. בנוסף לבדיקה זו ביצענו בדיקה איכותית לשינוי לחץ על ידי שליטה על מהירות הלחיצה 1( ככל שהלחיצה יותר מהירה לחץ הפיק הגבוה שהאמבו מייצר – עולה עד כדי 60 מיליבאר ויורד מהר מאוד ללחץ שרואים בגרפים לעיל שמתאים לנפח הלחיצה שבוצע. 2( כלומר ניסיון לשלוט על מהירות הלחיצה על מנת להאט את קצב בניית הלחץ לא יתן כאן מענה בגלל שמקור האוויר שלנו הוא "בלון" בנפח קבוע וכאשר מעבירים האוויר ממנו לריאות תוך הקטנת הנפח

- 4 -

המשותף של האמבו+ריאות, עולה הלחץ בהתאמה לערך קבוע. יתכן שמול ריאות אמיתיות זה מעט משתנה, כלומר אם הריאות מתנהגות כמו ה"ריאה המדמה" בניסוי נקבל הלחצים כמו בגרפים. אם הריאות לא מגיבות טוב, קשות לניפוח הלחץ עולה מהר מאוד כמעט ללא נפח אוויר שנכנס לריאות והמערכת תעצור ההנשמה ללא הגעה לנפח הנדרש למטופל. .5 תובנות לגבי מכשירי הנשמה בכלל והחלטות רפואיות א. מערכת האמבו שפותחה מבקרת למול החולה )ברמת הסנסור( רק את עליית הלחץ כתוצאה מנשיפה עצמאית למול הנשמה של המכשיר – במצב זה עוצרים ההנשמה למחזור וממשיכים שוב במחזור הבא. ב. מערכת זו אינה יודעת לזהות נשימה עצמית של מטופל, להעריך את עומק הנשימה ולהשלים את הנפח הנדרש לפי קביעת המטפל.
ג. לכן, המערכת אינה מסוגלת, בתצורתה הנוכחית, לתמוך במטופל ערני חצי נושם ולכן לשימוש במערכת נדרש להרדים את המטופל ולהכריח נשימת מכונה 1( מצב זה מסכן חיים כי אם המכונה מתקלקלת המטופל מת )לא יכול לנשום לבד( 2( לכן נדרש מוניטורינג רצוף של סימני חיים והבעיה שצופים הרופאים שיהיו חסרים גם מוניטורים כאלו.
ד. בנוסף, לחולי קורונה נדרשת בקרת הנשמה מבוססת לחץ – כלומר לנפח הריאות בלחץ קבוע ונמוך יחסית והמערכת שלנו מייצרת לחץ פורפורציוני לאורך הלחיצה שנקבע. ה. חולי קורונה צריכים שליטה על ריווי חמצן בתהליך ההנשמה עד כדי 100% והשליטה צריכה להיות של המנשם )שאין לנו( וזה חסרון נוסף. ו. עלה רעיון של החלפת מערכות הנשמה של חולים מורדמים/מונשמים ללא קורונה במכונה שלנו ופינוי המכונות המודרניות לחולי קורונה קשים. .6 משימות לטיפול
א. צוות תוכנה: עידכון הפרוטוקול הנשמה כפי שפורט לעיל. ב. צוות מכניקה: עידכון כיתוביות במארז כפי שפורט לעיל. ג. צוות ניהולי: להכניס המשימות לעבודה .7 בברכה,
זאב שניאורסון

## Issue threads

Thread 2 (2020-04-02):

AmboVent-1690-108/AmboVent #2: Post 3D print model file to 3D print Covid-19 group?

carolynnicita, 2020-04-02:
Could you please notify the Covid-19 3D printing group where we could find the model file(s) of the 3D printed parts for your design?  Thanks much!

the Discord room
https://discord.gg/GCTW4G

nimrod46, 2020-04-02:
Could you check if everything you need is [here](https://github.com/AmboVent/AmboVent/tree/master/Mechanical%20Design)? we just added the mechanical designs

KKaldis, 2020-04-02:
there are  *.step files, you can output with any software to stl

jejaffeTN, 2020-04-02:
Are CAD files available in other formats such as **DAE, OBJ or STL?** 

If not, and we convert them, may we post them here for others? 

Jonathan

closed 2020-04-02 by carolynnicita

jejaffeTN, 2020-04-02:
Closed without comment or answer by CarolynNicita
I do not understand.

salmanfarisvp, 2020-04-08:
- SolidWorks Files: [SolidWorks Pack and Go](https://github.com/AmboVent/AmboVent/tree/master/.Mechanics/Mechanism/SolidWorks%20Pack%20and%20Go)

- [Assembly in other formats](https://github.com/AmboVent/AmboVent/tree/master/.Mechanics/Mechanism/Assembly%20in%20other%20formats)

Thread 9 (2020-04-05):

AmboVent-1690-108/AmboVent #9: RST does something random

airbornemint, 2020-04-05:
This line should be `digitalRead(PIN_RST)`

https://github.com/AmboVent/AmboVent/blob/e889eb9853d8ce3cfa903381849227c7397c351b/.Software/Arduino%20Code/ventilation_machine/ventilation_machine.ino#L502

salam17, 2020-04-05:
RST is initialized to zero so the first digitalRead(RST) call is equivalent to digitalRead(pin_POT). On the next call. If the digitalRead returned zero, RST becomes 1 and the next read will be from pin_CUR, not an expected result.  RST is used to set the sign of wanted_cal_PWM so reading the rough position of pin_POT makes sense ( 0 for a position close to the minimum).  Should line 502 be:
RST = (1-digitalRead (pin_POT));  ?

nimrod46, 2020-04-06:
I fixed this line but keep in mind that this button is not currently in use, it's used only in calibration

closed 2020-04-06 by nimrod46

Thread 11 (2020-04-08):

AmboVent-1690-108/AmboVent #11: Use accepted best practices in code formatting to produce safe software

ElectricRCAircraftGuy, 2020-04-08:
I was just skimming your Arduino source code here, for instance: https://github.com/AmboVent/AmboVent/blob/master/.Software/Arduino%20Code/ventilation_machine/ventilation_machine.ino#L208

and I notice your formatting doesn't follow best practices to maximize for readability, maintainability, and safety. I recommend you change the code now and follow best practices as you write new code to minimize changes in the future. Here's a few examples:

1. Use curly braces after every single `if` statement or any type of loop. 
1. Use proper indentation.
1. With very very few exceptions, put each statement which ends with a semicolon on its own line.
1. Declare variables each on their own line.
1. Don't use integers for states; use enums

Instead of:

    if (millis()-last_TST_not_pressed>3000) { LED_USR(1); while (TST==1 || TST_pressed) { read_IO(); }   // wait for button release
                                              state=2;}

Do:

    if (millis() - last_TST_not_pressed > 3000) 
    { 
        LED_USR(1); 
        // wait for button release
        while (TST == 1 || TST_pressed) 
        { 
            read_IO(); 
        }   
        state = 2;
    }

But instead of that, even better, replace numbers and do this. Notice there's not a single "magic number" anymore. Everything is now named.

    #define DELAY_TIME_MS 3000

    enum states
    {
        STATE_OK = 0,
        STATE_ERROR = 1,
        STATE_AIR_IN = 2,
    };

    if (millis() - last_TST_not_pressed > DELAY_TIME_MS) 
    { 
        LED_USR(HIGH); 
        // wait for button release
        while (TST == true || TST_pressed) 
        { 
            read_IO(); 
        }   
        state = STATE_AIR_IN;
    }

Instead of this:

    case 4:     // toggle sync to patient
      if (patient_triggered_breath==1) display_text_2_lines("Sync to patient","ON  ");
      if (patient_triggered_breath==0) display_text_2_lines("Sync to patient","OFF  ");
      if (TST_pressed)  {
        patient_triggered_breath=1-patient_triggered_breath; delay(110);
        if (patient_triggered_breath==1) display_text_2_lines("Sync to patient","ON  ");
        if (patient_triggered_breath==0) display_text_2_lines("Sync to patient","OFF  ");
        delay (1500);
        exit_menu();
        }
      break;

Do this:

    case TOGGLE_SYNC_TO_PATIENT:
        if (patient_triggered_breath) 
        {
            display_text_2_lines("Sync to patient","ON  ");
        }
        else
        {
            display_text_2_lines("Sync to patient","OFF  ");
        }

        if (TST_pressed)  
        {
            patient_triggered_breath = 1 - patient_triggered_breath; 
            delay(110);

            if (patient_triggered_breath) 
            {
                display_text_2_lines("Sync to patient","ON  ");
            }
            else 
            {
                display_text_2_lines("Sync to patient","OFF  ");
            }
            delay (1500);
            exit_menu();
        }
        
        break;

nimrod46, 2020-04-09:
Well, believe me, I feel you, but this code was basically written in one day for POC, the one who wrote it just had to add more features as the time went by and he did not keep in mind code readability, flexibility, etc.

The idea of open source is for you guys to not just use this project as is, but to also improving it.
So you are more than welcome to suggest PR which we will review and push to this project (just like #14) :).

I will keep this issue open so more ppl will understand that this code is far from perfect and maybe even help improve this code.

giorakor, 2020-04-09:
you are correct. maorfr re-arranged the code beautifully and it is now the latest ver
after his fix - I am closing this issue
thanks for commenting

ElectricRCAircraftGuy, 2020-04-09:
Now that I know you're willing to accept feedback and merge PRs from others, I'll see if I can find some time one of these evenings to go through it myself and keep on improving things. 

Thanks all.

ElectricRCAircraftGuy, 2020-04-12:
@giorakor, please re-open this issue. I still see a ton to fix. I volunteer. You can assign me to this issue.

ElectricRCAircraftGuy, 2020-04-20:
PR #46 resolves a tiny portion of this issue

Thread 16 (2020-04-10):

AmboVent-1690-108/AmboVent #16: Solidworks files are not portable

mgaman, 2020-04-10:
For those of us working at home with open source CAD software, the SLDPRT and SLDASM files are unusable. 
Can you please export into some compatible format e.g. STEP.

SRC0991, 2020-04-10:
Hi, my friend

You can do two things for work with this files.
1. You can download Drawings to open SLDPRT and SLDASM files.
Here is the link: https://www.edrawingsviewer.com/download-edrawings
2. You can convert to CAD software such as STEP using CAD exchanger 
Here is the link: https://cadexchanger.com/downloads

mgaman, 2020-04-11:
Thanks. I tried cadexchanger and was able to import some SLDPRT and export in brep and stl format.
SLDDRW files are ignored, SLDASM sometimes yes, sometimes no.
There is a sizing issue e.g. Cadexchanger imports a SLDPRT file and the dimension tool shows it to be 206mm long. However I export the part as SfTL and open with CURA and the part seems to be >300mm long.
I assume that I'm messing up somewhere so I'll have to go back and RTFM.

justinclift, 2020-04-12:
As a data point, there are STEP format versions of some of the files in there.  eg:

* https://github.com/AmboVent/AmboVent/blob/a48090222f2ed3abc7753daacaff11675f97fa73/.Mechanics/Casing/AMBOVENT.STEP
* https://github.com/AmboVent/AmboVent/blob/a48090222f2ed3abc7753daacaff11675f97fa73/.Mechanics/Mechanism/Assembly%20in%20other%20formats/1690-20-8300%20%20REV7%20%2026.3.2020%20%2020_30.STEP

Haven't taken a look at them personally, more just pointing them out. :smile:

nimrod46, 2020-04-12:
If still have problems with the mechanic files feel free to reopen/open an issue

closed 2020-04-12 by nimrod46

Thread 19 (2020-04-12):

AmboVent-1690-108/AmboVent #19: Low memory available, stability problems may occur

ElectricRCAircraftGuy, 2020-04-12:
When I build the project for the Arduino Nano I see the following output in the Arduino IDE:
```
Sketch uses 18280 bytes (59%) of program storage space. Maximum is 30720 bytes.
Global variables use 1882 bytes (91%) of dynamic memory, leaving 166 bytes for local variables. Maximum is 2048 bytes.
Low memory available, stability problems may occur.
```

This is a problem, as it means the stack is nearly completely used up by global variables, so local variables in any scope or code section could potentially overflow the stack really easily. I think I can do some code cleanup to fix this, perhaps by moving string to progmem with the `F()` macro, or using other coding techniques. 

Read more on the `F()` macro here:
1. https://www.arduino.cc/reference/tr/language/variables/utilities/progmem/
1. https://www.baldengineer.com/arduino-f-macro.html

jsodergren, 2020-04-12:
For me, that warning went away with commit ae4205c.. on Apr 6.  
Building the Apr 6 version for a Nano:
```
Sketch uses 17810 bytes (57%) of program storage space. Maximum is 30720 bytes.
Global variables use 1518 bytes (74%) of dynamic memory, leaving 530 bytes for local variables. Maximum is 2048 bytes.
```
But it looks like the Apr 8 reformatting/cleanup commit apparently reverted the changes of the three previous commits.

Additionally, the F() macro is getting clobbered by redefining F for use as a PID parameter:
`#define F 5               // motion control feed forward`
I've changed the PID parameter #define to FF to work around this.

ElectricRCAircraftGuy, 2020-04-12:
Are you working with the team? Making one of these solo with their code? Something else? 

> But it looks like the Apr 8 reformatting/cleanup commit reverted the changes of the three previous commits.

That's important. That's too bad. Using git is a fairly complicated skill so it's easy to mess up.

> Additionally, the F() macro is getting clobbered by redefining F for use as a PID parameter:
> #define F 5 // motion control feed forward
> I've changed the PID parameter name to "FF" to work around this.

Good to know. We need to fix this. I'm about to start cleaning up the code but my first 2 PRs already touch like 230 files or something, so until they merge I'm afraid to change too much more. I'll end up touching nearly every line by the time I'm done and I don't want to mess up work underneath them. 

My 2 PRs waiting now are #18 and #20.

ElectricRCAircraftGuy, 2020-04-12:
If you're working on the code right now, watch out for my changes! If so, you should pull my #20 branch right now and rebase on top of it. Let me know if you're working on stuff so I can be aware.

jsodergren, 2020-04-12:
Good to know of your work and PRs.  I haven't submitted any PRs (yet); just trying to modify the released code slightly to work with our build (I'm part of a small team working to recreate the device for use in Alaska). Aside from the already-mentioned macro issue, I'm using a different LCD panel (NHD-0420D3Z 20x4) and have written a minimal library to use it with this code.

From what I can tell, the Apr 8 commit (a480902) reversed the changes made in commits 352b36a, e8fb1d9, and ae4205c. Here's the point right before those changes were reversed; this is what I'm currently working with: [https://github.com/AmboVent/AmboVent/tree/352b36a447adc2dabcf7890711da37fb903b46d6](https://github.com/AmboVent/AmboVent/tree/352b36a447adc2dabcf7890711da37fb903b46d6)

giorakor, 2020-04-12:
just released a new ver. that returned the lost functionality (accepted a PR that suggested readability improvements without noticing it was based on old ver.)
in this version -
- improved the code structure, memory use (75% now.. still warns.. but it is much better)
- added some new functions 
      - press test once during standby to run one cycle
      - ability to calibrate the env. pressure from the maint menu
      - option to set the breath cycle movement time

nimrod46, 2020-04-12:
Hi, thank you guys for your input, @giorakor improved the code a lot from the last commit and fix the merge #14 that was based on older version

Arie001, 2020-04-12:
I have just today  submitted  a new pcb . I plan on porting  the code to esp32 all the Libs used seem to be supported. A simple next gen pcb  will be esp32 no memory shortage and not running 24bit math on a 8 bit ATmel.  This is my solution a hardware upgrade for me to replace the nano with a esp and Jtag can start  if needed.

I  can have that version done by the end but I only have one ESp32-wroom that I can debug with .
I have a Jtag cable so it is normal code development  with breakpoints.

Sorry if it is a 10 pound hammer solution.

ElectricRCAircraftGuy, 2020-04-12:
@Arie001, the real problem was coding. Simply using progmem and the F() macro could decrease RAM usage from 90% to 30%, for instance.

ElectricRCAircraftGuy, 2020-04-13:
Note: please don't close this issue until at least all strings have been surrounded by the F() macro and all large const arrays or structs (if any) have been moved to progmem.

Xexnon, 2020-04-13:
> I have just today submitted a new pcb . I plan on porting the code to esp32 all the Libs used seem to be supported. A simple next gen pcb will be esp32 no memory shortage and not running 24bit math [...]

Porting the code to esp32 you might experience issues with ADCs on esp32.  The ADC values are non-linear. You get the same ADC resolution for high and low voltages. Then also the error between actual measurement and value measure by ADC is about 10%

Arie001, 2020-04-13:
I do not know where you get your esp32  or but a esp can read a2d Just Fine no where near 400 counts error   If all it has to do is measure a a2d of a pot . Advise a rc filter cap on the a2d pin  so are you saying .And No at 0db is not the same as -3db put into the same a2d 

We are talking about memory  92% vs 5%

Platform IO
RAM:   [=         ]   5.2% (used 17076 bytes from 327680 bytes)
Flash: [==        ]  18.8% (used 246093 bytes from 1310720 bytes)

 i2C 4 Leds  3 switches 3 Pots and a analog  feedback   is not pushing the limit  . It is alive on the uart at 115200

Xexnon, 2020-04-13:
> I do not know where you get your esp32 or but a esp can read a2d Just Fine no where near 400 counts error If all it has to do is measure a a2d of a pot . Advise a rc filter cap on the a2d pin so are [...]

Wow..  Makes a lot of sense...  Seems like you're done porting it to esp32

Xexnon, 2020-04-13:
> I do not know where you get your esp32 or but a esp can read a2d Just Fine no where near 400 counts error If all it has to do is measure a a2d of a pot . Advise a rc filter cap on the a2d pin so are [...]
would you mind sharing the code and pcb design

Arie001, 2020-04-14:
off topic

The ESP32 has a native range of 1.1v Full so 1.1/4096 is scale if you measure on 3.3v full scale it is 3.3 /4096 -6db . To say the error is the same no matter if I use 1.1v or 3.3v shows a lack of Knowledge.Do you claim I put 500mv dc onto a a A2D I get  either 450mv or 650mv no matter if I am on a 1.1v range ore 3.3V.The Error is the same no matter The Range.The a2d in not 100 Linear 
I Know that.If you look people are able to measure 0.02v . 12 years back when I worked for Intel the Chips were not 100% Linear I debugged  many a A2D problem on old LTX VLSI testers.
Been there done That .

On topic 

my code is the same  code as the this project   imported  to platform io  I changed  the the servo library  to  https://www.arduinolibraries.info/libraries/esp32-servo  it did not compile  it had issues with the variable  called index char * to int conversion  fail . I renamed Index  Index_arie  it compiled .download. I only have esp32 bare modules not a devkit . 

For Idea  of  how I will be doing the circuit  please see 

https://arie-lashansky.info/corona/carona_HX711.pdf    

My Style is  to be very careful  Esp   top right   

2*esp pots page 1 bottom left  dual  pots below esp ( Backup Motor feed Back too) 
2 voltage monitors  ( no hx711 the pressure sensor is  is not nxp but the ) 
2*te sensor  one on 3v one 3v Aux one to main esp 1 to Aux 
2 power supply  may be the idea on page 2. 
Display  is a TFT 2.5 inch or 3.2 Inch spi  touch  display.

Who knows I may even look at a second full mechanical  backup.second Ambo bag

As my Input is not wanted or needed here. I all allowing myself  to diverge from the design  done by the 40 experts engineering and medical experts .   

From my circuit  my style is clear no way in hell will I put a pull up to 4.7k pull up to 5v on a device  that  the datasheet says max IO voltage in VDD . I put two sensors in the box and  box not 1 .

https://www.te.com/commerce/DocumentDelivery/DDEController?Action=showdoc&DocId=Data+Sheet%7FMS5803-01BA%7FB3%7Fpdf%7FEnglish%7FENG_DS_MS5803-01BA_B3.pdf%7FCAT-BLPS0038   ( page 5  max allowable voltage on pins SCL and SDA) 

Note  Jumpers  allow cheap and 100% backup ( They are  be wire links)

It is a Question  of how you view your design  . I am not a mechanical engineer and my software skills are limited .

Just a unemployed  Electronics person that has over 30 years no second degree in Engineering not 
doing a Public relations  exercise for  Israeli defense company of Magaen David Adom

Who I am is clear where I come from is clear I have even added my resume the one that 
has not found work in over a year and note even my resume is clear I do not Lie and call myself 
things I am not qualified like a Degree engineer. 

Who I am is clear as daylight did I know a closed pcb was in the works for this design yes. 
was if part of the Idea to fork the design yes most definitely. Part of open source design 
nobody owns the IP.

Did I need need to generate my own DXF  Yes never done before my me in a design where I was 
unable to get DXF. 
I my pcb missing a mounting hole in the bottom right corner  Yes  no hole in the metalwork.
Is my Switch to near to the mounting  hole (Test ) I did not put switch  in that position Ambovent did.
Have I uses witches with a 8mm head not 6.5mm yes  No cheap option  Alpms .

Mix This the two pcbs  below remove the (nxp pressure sensors and Arduino). I will be a 4 layer board.3v 3vaux 5v and 5v_aux  12v 12aux on split planes.

 https://grabcad.com/library/ambervent_pcb-baisic-placement-1 
https://grabcad.com/library/pcb-exported-from-kicad-1  
This is placement of the extender  

[‏‏arie_lashansky_cv.docx](https://github.com/AmboVent-1690-108/AmboVent/files/4473039/arie_lashansky_cv.docx)
[carona_HX711.pdf](https://github.com/AmboVent-1690-108/AmboVent/files/4473046/carona_HX711.pdf)

ElectricRCAircraftGuy, 2020-04-14:
> As my Input is not wanted or needed here. I all allowing myself to diverge from the design done by the 40 experts engineering and medical experts .

Hey we didn't say that. I'm just a random guy who started poking at this project a few days ago--not part of the team. All I know is, before I go changing something I have no control over, I'd like to get the code cleaned up. My goal: clean the code. Make it robust. If I do that. I will be happy. Based on what I see, the Nano is more than adequate. So...back to cleaning the code and making it better. They did a great job, I just want to contribute what I can. 

And I hope you can find good work. Remember to use LinkedIn, network, and practice interviewing skills. Also have a solid resume and showcase your skills with past and present projects--personal or otherwise.

Xexnon, 2020-04-14:
> off topic
> 
> The ESP32 has a native range of 1.1v Full so 1.1/4096 is scale if you measure on 3.3v full scale it is 3.3 /4096 -6db . To say the error is the same no matter if I use 1.1v or 3.3v shows a lack of Knowledge.Do you claim I put 500mv dc onto a a A2D I get either 450mv or 650mv no matter if I am on a 1.1v range ore 3.3V.The Error is the same no matter The Range.The a2d in not 100 Linear
> I Know that.If you 
> 
> my code is the same code as the this project imported to platform io I changed the the servo library to https://www.arduinolibraries.info/libraries/esp32-servo it did not compile it had issues with the variable called index char * to int conversion fail . I renamed Index Index_arie it compiled .download. I only have esp32 bare modules not a devkit .
> 

Had the same issue while porting to esp32 yesterday, the servo, and LCD libraries are incompatible.. 

Still  had the issue with `Index` on line 138.. I think it should be renamed to something else on the main code for people who will want to port the code to other platforms

ElectricRCAircraftGuy, 2020-04-14:
Please open a new issue and link to it here. I need some clarity. What variable where needs to be renamed to what, due to what error?

Here's line 138: https://github.com/AmboVent-1690-108/AmboVent/blob/master/3-Software/Arduino/ventilation_machine/ventilation_machine.ino#L138

Arie001, 2020-04-14:
I renamed the Index Issue as part of my Debug in getting it to compile I do it often to find where I have made changes. It is a way of me finding my Changes it is part of my workflow. I do not leave it that way.To search and replace Index_arie with Main_index is simple . It is part of debugging.

Index is in 24 places in the code that is about 750 lines I use that method for Debug why do you think I am not uploading the code . I do not even Know on what Lib Index  was defined Char* 

The Time was spent to see the memory Footprint  no more no Less . I am not a Embedded Software 
person. If I touch Code that I have not Read or tried to understand  any Line I mark with my name saves me getting mixed up.

I am working in a environment called Platform IO on Visual Studio code on a Part ESP32 not related 
to Arduino Nano  Atmel. Why Open a Issue where the Issue was created by me Porting From Arduino Ide to Platform IO it is a issue for me nobody else, Like the person looking for 

 I needed to Change Sevo. to the ESP version  the simple solution was the one I took it.
My design I have not even decided if I want to use a base esp like my Hx711 or a module or if 
I want to make it hardware redundant like the HX711 why open Issues that do not exist  

The Part from the Sevo32 Lib is not the problem but shows how hard it is to Find

[image]

[image]
[image]

Arie001, 2020-04-14:
This is all I wanted to see no more no less

[image]

Arie001, 2020-04-21:
This issue can be closed current version  only uses 1k so 1k Free

https://github.com/AmboVent-1690-108/AmboVent/tree/master/3-Software/Arduino/ventilation_machine

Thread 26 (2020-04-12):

AmboVent-1690-108/AmboVent #26: New Option PCB

Arie001, 2020-04-12:
Here is a new option  for a PCB 

https://github.com/Arie001/ambovent_pcb_Rev_Arie/tree/master/respirator-control_rev2

Please review Kicad  I have checked it in Fusion 360 .
I did not Find good cheap switches  that fit the small holes.
Only one three extra Parts for 12v .

DRC was run at 0.5mm .  Fails RGB Led the footprint  and Sw1 is near the corner screw
Note The Arduino and the Module I2C  was not put on the PCB as I want to keep it simple no smd soldering.

I think it is a Major step up. 
I can have a board ready in a few hours I am in Modiin  .

The  Board is supported 3 corners the bottom right is not supported No hole Below  the the Hole 
for the sensor.

I have exported the Step Not the Height of the Lcd may not be correct .

[image]

I use dry Film Etch  
054-6597555

salam17, 2020-04-12:
Not sure where this rant belongs, but here goes: Almost none of the DIY ventilator projects I see have alarms or battery back up, despite the fact that if you need a DIY ventilator you are also short staffed by definition; at a bare minimum, should power be lost when there are no eyes on the patient a  battery powered alarm is needed; it could save a life. Unless there is a UPS, one that has an alarm of its own, I see this as a critical requirement. There is plenty of room on this PC for a coin cell and a beeper.

nimrod46, 2020-04-12:
> ition; at a bare minimum, should power be lost when there are no eyes on the patient a battery powered alarm is needed; it could save a life. Unless there is a UPS, one that has an alarm of its own, [...]

That's correct we are using UPS  and a battery as a backup to **keep the system running** (not just for alarm). 

Someone did design for as a new board that will contain all of these things and **much more** but it will be ready only in a weak, @Arie001 I am contacting you NOW is will be a huge help for as.

Arie001, 2020-04-12:
See the PCB  I made see the PCB in the production directory . 
See the  gerber  f copper in the  github .I have spent time doing a high quality work .
No a 5 min pcb one that a person can be proud of.

Ok it was not me that claimed 2 hour battery life and never measured the battery voltage.If you claim 2 hours how do you know the battery was charged . Or was it Just that most of the Team wanted to get the positive press.   

I added 2 resistors and one Cap to a unused pin A7 .
Find Fault with the PCB it is High Volume ready done by a skilled Pcb Expert. Not somebody that does not Know the Difference between Front and Back Gerber Files.

I have no Issue to not have the PCB in the main.

Lets say you can  run this on a 12v 7ah  alarm led acid battery  for two hours . It is sort of Important 
to Know the battery is at 12v and not 10v.

Please download the original pcb a 1 layer board now explain how to solder the cap on the input if the board if the pads are covered. Fcu

Arie001, 2020-04-12:
Nimrod see the Board

Arie001, 2020-04-12:
it is about to be updated to esp32 in the next 2 days so memory issues will be history

Arie001, 2020-04-12:
Call Me  0546597555

Arie001, 2020-04-13:
I have Done Some extra Editing . To stop the Cables Falling out  the Headers face up just the Lcd  cable  needs securing  Hot glue  or silicon . I added a Tie down point
[image]

Arie001, 2020-04-15:
Here Is picture of my Current pcb My Fork has changed al lot But the Two parts that I can update the  Board Is the Pots and the Push Button switches> I am Moving away from the Idea of physical
Pots. 

I will Not we working on This  on the 16 of April  I an attending .
https://www.thethingsnetwork.org/conference/
 Online 
I am still TTN Modiin 
https://www.thethingsnetwork.org/community/modiin/

 
Arie
 
[image]

https://grabcad.com/library/ambovent-with-metalwork-face-1

Arie001, 2020-05-02:
Do not use until 3v level shift is added 2 * 2n7002 and 2 resistors

Arie001, 2020-05-06:
3v level shift done on pcb

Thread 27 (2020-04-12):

AmboVent-1690-108/AmboVent #27: Resolve all warnings

ElectricRCAircraftGuy, 2020-04-12:
I just built the latest (from my PR #20), and there are dozens of warnings to fix.

```
/home/alexa/Downloads/Install_files/Arduino/arduino-1.8.8/arduino-builder -dump-prefs -logger=machine -hardware /home/alexa/Downloads/Install_files/Arduino/arduino-1.8.8/hardware -hardware /home/alexa/.arduino15/packages -tools /home/alexa/Downloads/Install_files/Arduino/arduino-1.8.8/tools-builder -tools /home/alexa/Downloads/Install_files/Arduino/arduino-1.8.8/hardware/tools/avr -tools /home/alexa/.arduino15/packages -built-in-libraries /home/alexa/Downloads/Install_files/Arduino/arduino-1.8.8/libraries -libraries /home/alexa/Arduino/libraries -fqbn=arduino:avr:nano:cpu=atmega328 -ide-version=10808 -build-path /tmp/arduino_build_472179 -warnings=all -build-cache /tmp/arduino_cache_729925 -prefs=build.warn_data_percentage=75 -prefs=runtime.tools.avr-gcc.path=/home/alexa/Downloads/Install_files/Arduino/arduino-1.8.8/hardware/tools/avr -prefs=runtime.tools.avr-gcc-5.4.0-atmel3.6.1-arduino2.path=/home/alexa/Downloads/Install_files/Arduino/arduino-1.8.8/hardware/tools/avr -prefs=runtime.tools.arduinoOTA.path=/home/alexa/Downloads/Install_files/Arduino/arduino-1.8.8/hardware/tools/avr -prefs=runtime.tools.arduinoOTA-1.2.1.path=/home/alexa/Downloads/Install_files/Arduino/arduino-1.8.8/hardware/tools/avr -prefs=runtime.tools.avrdude.path=/home/alexa/Downloads/Install_files/Arduino/arduino-1.8.8/hardware/tools/avr -prefs=runtime.tools.avrdude-6.3.0-arduino14.path=/home/alexa/Downloads/Install_files/Arduino/arduino-1.8.8/hardware/tools/avr -verbose /home/alexa/dev/AmboVent/AmboVent/3-Software/Arduino/ventilation_machine/ventilation_machine.ino
/home/alexa/Downloads/Install_files/Arduino/arduino-1.8.8/arduino-builder -compile -logger=machine -hardware /home/alexa/Downloads/Install_files/Arduino/arduino-1.8.8/hardware -hardware /home/alexa/.arduino15/packages -tools /home/alexa/Downloads/Install_files/Arduino/arduino-1.8.8/tools-builder -tools /home/alexa/Downloads/Install_files/Arduino/arduino-1.8.8/hardware/tools/avr -tools /home/alexa/.arduino15/packages -built-in-libraries /home/alexa/Downloads/Install_files/Arduino/arduino-1.8.8/libraries -libraries /home/alexa/Arduino/libraries -fqbn=arduino:avr:nano:cpu=atmega328 -ide-version=10808 -build-path /tmp/arduino_build_472179 -warnings=all -build-cache /tmp/arduino_cache_729925 -prefs=build.warn_data_percentage=75 -prefs=runtime.tools.avr-gcc.path=/home/alexa/Downloads/Install_files/Arduino/arduino-1.8.8/hardware/tools/avr -prefs=runtime.tools.avr-gcc-5.4.0-atmel3.6.1-arduino2.path=/home/alexa/Downloads/Install_files/Arduino/arduino-1.8.8/hardware/tools/avr -prefs=runtime.tools.arduinoOTA.path=/home/alexa/Downloads/Install_files/Arduino/arduino-1.8.8/hardware/tools/avr -prefs=runtime.tools.arduinoOTA-1.2.1.path=/home/alexa/Downloads/Install_files/Arduino/arduino-1.8.8/hardware/tools/avr -prefs=runtime.tools.avrdude.path=/home/alexa/Downloads/Install_files/Arduino/arduino-1.8.8/hardware/tools/avr -prefs=runtime.tools.avrdude-6.3.0-arduino14.path=/home/alexa/Downloads/Install_files/Arduino/arduino-1.8.8/hardware/tools/avr -verbose /home/alexa/dev/AmboVent/AmboVent/3-Software/Arduino/ventilation_machine/ventilation_machine.ino
Using board 'nano' from platform in folder: /home/alexa/Downloads/Install_files/Arduino/arduino-1.8.8/hardware/arduino/avr
Using core 'arduino' from platform in folder: /home/alexa/Downloads/Install_files/Arduino/arduino-1.8.8/hardware/arduino/avr
Detecting libraries used...
/home/alexa/Downloads/Install_files/Arduino/arduino-1.8.8/hardware/tools/avr/bin/avr-g++ -c -g -Os -w -std=gnu++11 -fpermissive -fno-exceptions -ffunction-sections -fdata-sections -fno-threadsafe-statics -Wno-error=narrowing -flto -w -x c++ -E -CC -mmcu=atmega328p -DF_CPU=16000000L -DARDUINO=10808 -DARDUINO_AVR_NANO -DARDUINO_ARCH_AVR -I/home/alexa/Downloads/Install_files/Arduino/arduino-1.8.8/hardware/arduino/avr/cores/arduino -I/home/alexa/Downloads/Install_files/Arduino/arduino-1.8.8/hardware/arduino/avr/variants/eightanaloginputs /tmp/arduino_build_472179/sketch/ventilation_machine.ino.cpp -o /dev/null
/home/alexa/Downloads/Install_files/Arduino/arduino-1.8.8/hardware/tools/avr/bin/avr-g++ -c -g -Os -w -std=gnu++11 -fpermissive -fno-exceptions -ffunction-sections -fdata-sections -fno-threadsafe-statics -Wno-error=narrowing -flto -w -x c++ -E -CC -mmcu=atmega328p -DF_CPU=16000000L -DARDUINO=10808 -DARDUINO_AVR_NANO -DARDUINO_ARCH_AVR -I/home/alexa/Downloads/Install_files/Arduino/arduino-1.8.8/hardware/arduino/avr/cores/arduino -I/home/alexa/Downloads/Install_files/Arduino/arduino-1.8.8/hardware/arduino/avr/variants/eightanaloginputs -I/home/alexa/Downloads/Install_files/Arduino/arduino-1.8.8/hardware/arduino/avr/libraries/EEPROM/src /tmp/arduino_build_472179/sketch/ventilation_machine.ino.cpp -o /dev/null
/home/alexa/Downloads/Install_files/Arduino/arduino-1.8.8/hardware/tools/avr/bin/avr-g++ -c -g -Os -w -std=gnu++11 -fpermissive -fno-exceptions -ffunction-sections -fdata-sections -fno-threadsafe-statics -Wno-error=narrowing -flto -w -x c++ -E -CC -mmcu=atmega328p -DF_CPU=16000000L -DARDUINO=10808 -DARDUINO_AVR_NANO -DARDUINO_ARCH_AVR -I/home/alexa/Downloads/Install_files/Arduino/arduino-1.8.8/hardware/arduino/avr/cores/arduino -I/home/alexa/Downloads/Install_files/Arduino/arduino-1.8.8/hardware/arduino/avr/variants/eightanaloginputs -I/home/alexa/Downloads/Install_files/Arduino/arduino-1.8.8/hardware/arduino/avr/libraries/EEPROM/src -I/home/alexa/Downloads/Install_files/Arduino/arduino-1.8.8/libraries/Servo/src /tmp/arduino_build_472179/sketch/ventilation_machine.ino.cpp -o /dev/null
/home/alexa/Downloads/Install_files/Arduino/arduino-1.8.8/hardware/tools/avr/bin/avr-g++ -c -g -Os -w -std=gnu++11 -fpermissive -fno-exceptions -ffunction-sections -fdata-sections -fno-threadsafe-statics -Wno-error=narrowing -flto -w -x c++ -E -CC -mmcu=atmega328p -DF_CPU=16000000L -DARDUINO=10808 -DARDUINO_AVR_NANO -DARDUINO_ARCH_AVR -I/home/alexa/Downloads/Install_files/Arduino/arduino-1.8.8/hardware/arduino/avr/cores/arduino -I/home/alexa/Downloads/Install_files/Arduino/arduino-1.8.8/hardware/arduino/avr/variants/eightanaloginputs -I/home/alexa/Downloads/Install_files/Arduino/arduino-1.8.8/hardware/arduino/avr/libraries/EEPROM/src -I/home/alexa/Downloads/Install_files/Arduino/arduino-1.8.8/libraries/Servo/src -I/home/alexa/Downloads/Install_files/Arduino/arduino-1.8.8/hardware/arduino/avr/libraries/Wire/src /tmp/arduino_build_472179/sketch/ventilation_machine.ino.cpp -o /dev/null
/home/alexa/Downloads/Install_files/Arduino/arduino-1.8.8/hardware/tools/avr/bin/avr-g++ -c -g -Os -w -std=gnu++11 -fpermissive -fno-exceptions -ffunction-sections -fdata-sections -fno-threadsafe-statics -Wno-error=narrowing -flto -w -x c++ -E -CC -mmcu=atmega328p -DF_CPU=16000000L -DARDUINO=10808 -DARDUINO_AVR_NANO -DARDUINO_ARCH_AVR -I/home/alexa/Downloads/Install_files/Arduino/arduino-1.8.8/hardware/arduino/avr/cores/arduino -I/home/alexa/Downloads/Install_files/Arduino/arduino-1.8.8/hardware/arduino/avr/variants/eightanaloginputs -I/home/alexa/Downloads/Install_files/Arduino/arduino-1.8.8/hardware/arduino/avr/libraries/EEPROM/src -I/home/alexa/Downloads/Install_files/Arduino/arduino-1.8.8/libraries/Servo/src -I/home/alexa/Downloads/Install_files/Arduino/arduino-1.8.8/hardware/arduino/avr/libraries/Wire/src -I/home/alexa/Arduino/libraries/SparkFun_MS5803-14BA_Breakout_Arduino_Library-master/src /tmp/arduino_build_472179/sketch/ventilation_machine.ino.cpp -o /dev/null
/home/alexa/Downloads/Install_files/Arduino/arduino-1.8.8/hardware/tools/avr/bin/avr-g++ -c -g -Os -w -std=gnu++11 -fpermissive -fno-exceptions -ffunction-sections -fdata-sections -fno-threadsafe-statics -Wno-error=narrowing -flto -w -x c++ -E -CC -mmcu=atmega328p -DF_CPU=16000000L -DARDUINO=10808 -DARDUINO_AVR_NANO -DARDUINO_ARCH_AVR -I/home/alexa/Downloads/Install_files/Arduino/arduino-1.8.8/hardware/arduino/avr/cores/arduino -I/home/alexa/Downloads/Install_files/Arduino/arduino-1.8.8/hardware/arduino/avr/variants/eightanaloginputs -I/home/alexa/Downloads/Install_files/Arduino/arduino-1.8.8/hardware/arduino/avr/libraries/EEPROM/src -I/home/alexa/Downloads/Install_files/Arduino/arduino-1.8.8/libraries/Servo/src -I/home/alexa/Downloads/Install_files/Arduino/arduino-1.8.8/hardware/arduino/avr/libraries/Wire/src -I/home/alexa/Arduino/libraries/SparkFun_MS5803-14BA_Breakout_Arduino_Library-master/src -I/home/alexa/Arduino/libraries/Arduino-LiquidCrystal-I2C-library-master /tmp/arduino_build_47217 [... cut ...]
Using library Arduino-LiquidCrystal-I2C-library-master in folder: /home/alexa/Arduino/libraries/Arduino-LiquidCrystal-I2C-library-master (legacy)
Using library ArduinoUniqueID in folder: /home/alexa/Arduino/libraries/ArduinoUniqueID (legacy)
/home/alexa/Downloads/Install_files/Arduino/arduino-1.8.8/hardware/tools/avr/bin/avr-size -A /tmp/arduino_build_472179/ventilation_machine.ino.elf
Sketch uses 18412 bytes (59%) of program storage space. Maximum is 30720 bytes.
Global variables use 1046 bytes (51%) of dynamic memory, leaving 1002 bytes for local variables. Maximum is 2048 bytes.

```

nimrod46, 2020-04-13:
Fixed

ElectricRCAircraftGuy, 2020-04-14:
I just built your latest changes. 6 warnings still remain:
```
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

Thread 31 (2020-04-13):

AmboVent-1690-108/AmboVent #31: Use enums where able; C-style namespace them properly

ElectricRCAircraftGuy, 2020-04-13:
This is a sub-issue of #11. Don't close #11 until all sub-issues are resolved. 

Use enums wherever they make sense instead of constants or #defines. Also, namespace them by putting their categorical name before their specific name, separated by an underscore. 

Instead of:

```
enum main_states : byte
{
  STBY_STATE,
  BREATH_STATE,
  MENU_STATE
};
```

Do:

Use 3 slashes /// to signify "doxygen" style comments above members (good practice even if you don't generate doxygen). See more examples in my file here: https://github.com/ElectricRCAircraftGuy/eRCaGuy_dotfiles/blob/master/git%20%26%20Linux%20cmds%2C%20help%2C%20tips%20%26%20tricks%20-%20Gabriel.txt

```
enum main_states : byte
{
  // Use explicit name, and explicitly set 1st element to 0
  /// some useful description
  STATE_STANDBY = 0, 
  /// some useful description
  STATE_BREATH,
  /// some useful description
  STATE_MENU, 
  /// Not a state! Use this if you need the total number of enums in this type
  STATE_COUNT, // trailing comma on last elment is just fine
};
```

ElectricRCAircraftGuy, 2020-04-13:
I will help with this. Just want to teach the principle too is all.

nimrod46, 2020-04-13:
Just so you know, enums are type definition, not a list, so the name should be `main_state` for instance

ElectricRCAircraftGuy, 2020-04-13:
Fixed description.

ElectricRCAircraftGuy, 2020-04-13:
@nimrod46, I'm also accustomed to using `typedef`s when writing C, and many organizations require `enum class`es when using C++, but I think the C enum is just fine, but since Arduino is technically C++, it allows a simplified syntax without `typedef`. 

In C I'd add `_t` to the end of the enum type. Ex:

```
typedef enum main_state_e
{
  // Use explicit name, and explicitly set 1st element to 0
  /// some useful description
  MAIN_STATE_STANDBY = 0, 
  /// some useful description
  MAIN_STATE_BREATH,
  /// some useful description
  MAIN_STATE_MENU, 
  /// Not a state! Use this if you need the total number of enums in this type
  MAIN_STATE_COUNT, // trailing comma on last elment is just fine
} main_state_t;
```
Then
```
main_state_t main_state = MAIN_STATE_STANDBY;
```
 We can add the `_t` if you like too to specify it's a type, but since we don't need the `typedef` in C++, I'm fine without it too. @nimrod46 , let me know if you have a preference.

nimrod46, 2020-04-13:
@ElectricRCAircraftGuy I prefer without the `_t` the current main state should be `current_main_state `.
I think its the best practice to name it like that anyway

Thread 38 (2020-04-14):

AmboVent-1690-108/AmboVent #38: Solid works version issue

labeneator, 2020-04-14:
I have a colleague who has solidworks 2019 installed but can't open the files due to a 'future version' error. This seems to be a [common issue ](https://forum.solidworks.com/community/faqs/blog/2017/12/22/why-am-i-getting-a-future-version-error-when-i-try-to-open-a-file) requiring one to use a later solid works. Is it possible to use an earlier version to save the file or use a vendor neutral file format?

Email from the said person in verbatim

---

> Thanks for the links to the CAD files for the trial project. I hope we can collaborate so we can try out any other designs for equipment that will alleviate the current medical equipment availability. 
> 
> I was able to access the zip file containing the Solidworks files. However, they are tagged as 'future version' meaning I can't open the attachments with my current Solidworks 2019.

---

Thanks

ElectricRCAircraftGuy, 2020-04-14:
I haven't used SolidWorks in 5+ years, so someone else chime in too please, but I'm pretty sure Solid Works goes to great lengths to ensure this is the case, and there may not be any work-around. When I was using a newer version of SolidWorks in 2013, there was absolutely no way to save it in an older format, specifically to force you to buy a license for the newer version so you don't have to. Therefore, a common strategy was to keep the same version for as long as possible between upgrades.

labeneator, 2020-04-14:
There seems to be a way to use vendor neutral files: 
 - https://forum.solidworks.com/thread/230295
 -  https://www.youtube.com/watch?v=FFrOpYIPtpk
 -  https://help.solidworks.com/2019/English/SolidWorks/sldworks/c_previous_release_interoperability.htm

However, you do seem to lose flexibility in editing the vendor neutral files. Perhaps we can have both file options published for better coverage.

nimamoslemy, 2020-05-01:
Hi, we are a team that needs your feedback to complete our idea.
Please visit our pages and comment on it. 
[github](https://github.com/nimamoslemy/ventilator)
[gitlab](https://gitlab.com/nimamoslemy/avp-ventilator)

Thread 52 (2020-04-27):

AmboVent-1690-108/AmboVent #52: Access to Materials

aligbenewton7, 2020-04-27:
Please, find attached a list of the materials I couldn't find around.
[Ambovent BOM (parts list)_check 3 sheets.xlsx](https://github.com/AmboVent-1690-108/AmboVent/files/4541308/Ambovent.BOM.parts.list._check.3.sheets.xlsx)

salam17, 2020-04-28:
In stock but pricier at Amazon: https://www.amazon.com/Dorman-742-600-Window-Lift-Motor/dp/B000E35WEC/ref=sr_1_1?crid=E9W6ABV6G81B&dchild=1&keywords=dorman+742-600&qid=1588098679&s=automotive&sprefix=dorman+742-%2Cautomotive%2C147&sr=1-1

aligbenewton7, 2020-04-28:
Greeting Team,

Please, where do I find these materials? I can't get them in Nigeria.

Part Quantity מספר יצרן Materials Measurements
0.5" HEX ID x 1.125" OD x 0313" 1 217-2734   VEXpro
Arm Left 1
Polycarbonate : t=6 180x70x6
Arm Right 1   Polycarbonate : t=6 180x70x6
Arm Standoff 3
ABS Printed DIA12x15
Inner Adapter 1   Polycarbonate : t=6 / ABS Printed DIA40x6
Hex Shaft 1
AL5052-H32 / AL6061-T6 HEX12.7x27.94
Hex Spacer 1   AL5052-H32 / AL6061-T6 DIA19.05x9
Poly Upper Base 1
Polycarbonate : t=6 345x264.12x6
Poly Buttom Base 1   Polycarbonate : t=6 345x264.12x6
Profile Base 2
Any Aluminium 25x25x2; L=264.12
Profile Engine 1   Any Aluminium 40x40x3; t=2/3
Wall Right 1
Polycarbonate : t=6 136x81x6
Wall Left 1   Polycarbonate : t=6 136x81x6
Spacer 1 2
AL5052-H32 / AL6061-T6 DIA12x40
Spacer 2 1   AL5052-H32 / AL6061-T6 DIA15.88x7.21
Adapter 1
ABS printed 46.6x30x22.3
Adapter Small 1   ABS printed DIA21x18
Top Plate 1
Polycarbonate : t=6 200x188x6
Buttom Plate 1   Polycarbonate : t=6 200x188x6
Spacer 4
AL5052-H32 / AL6061-T6 DIA12x50
Arm Left REV.2 1   Polycarbonate : t=6
Wall Left REV.2 1
Polycarbonate : t=6
Wall Right REV.2 1   Polycarbonate : t=6
Spacer 1
ABS Printed DIA29x3.65

Casing

Arie001, 2020-05-03:
This is Arie I am not part of the Ambovent Team  here is my Quick Google search  https://www.trilineng.com/about-us/   Triline Nigeria Limited   can create the Items From stock  Polycarbonate.

 You will need to supply them the files  the printed parts need a 3d printer.

https://www.finelib.com/business/printing-and-publishing/3d-printing-services

I think one can try a Automotive  Window motor . I do not Know if anybody has made a DXF for the whole Items Laser cut.

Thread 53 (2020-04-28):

AmboVent-1690-108/AmboVent #53: Step by Step Guide?

salmanfarisvp, 2020-04-28:
Hi, This is not an issue.

Do we have any step by step by build guide for the AmboVent? I found the **AmboVent System Detailed Description - English 2.4.2020.pdf** , but it doesn't include basic things like instructions for the assembly..etc. 

Thanks.

Arie001, 2020-05-03:
Tell me what you need I hope to be in Bangalore soon after the covid19 ends . I do not think 
a step by step exists as only one prototype exists.  Even the BOM is a very gray area. Like analog feedback of motor position . How are they doing it is it a simple Pot or a proper sensor.For example
I was thinking of 3d Printed Sensor using a  Hall element OH49E SS49E Hall sensor  and a magnet .
sub less than a dollar or some IR method.

salmanfarisvp, 2020-05-18:
Did you completed the build?

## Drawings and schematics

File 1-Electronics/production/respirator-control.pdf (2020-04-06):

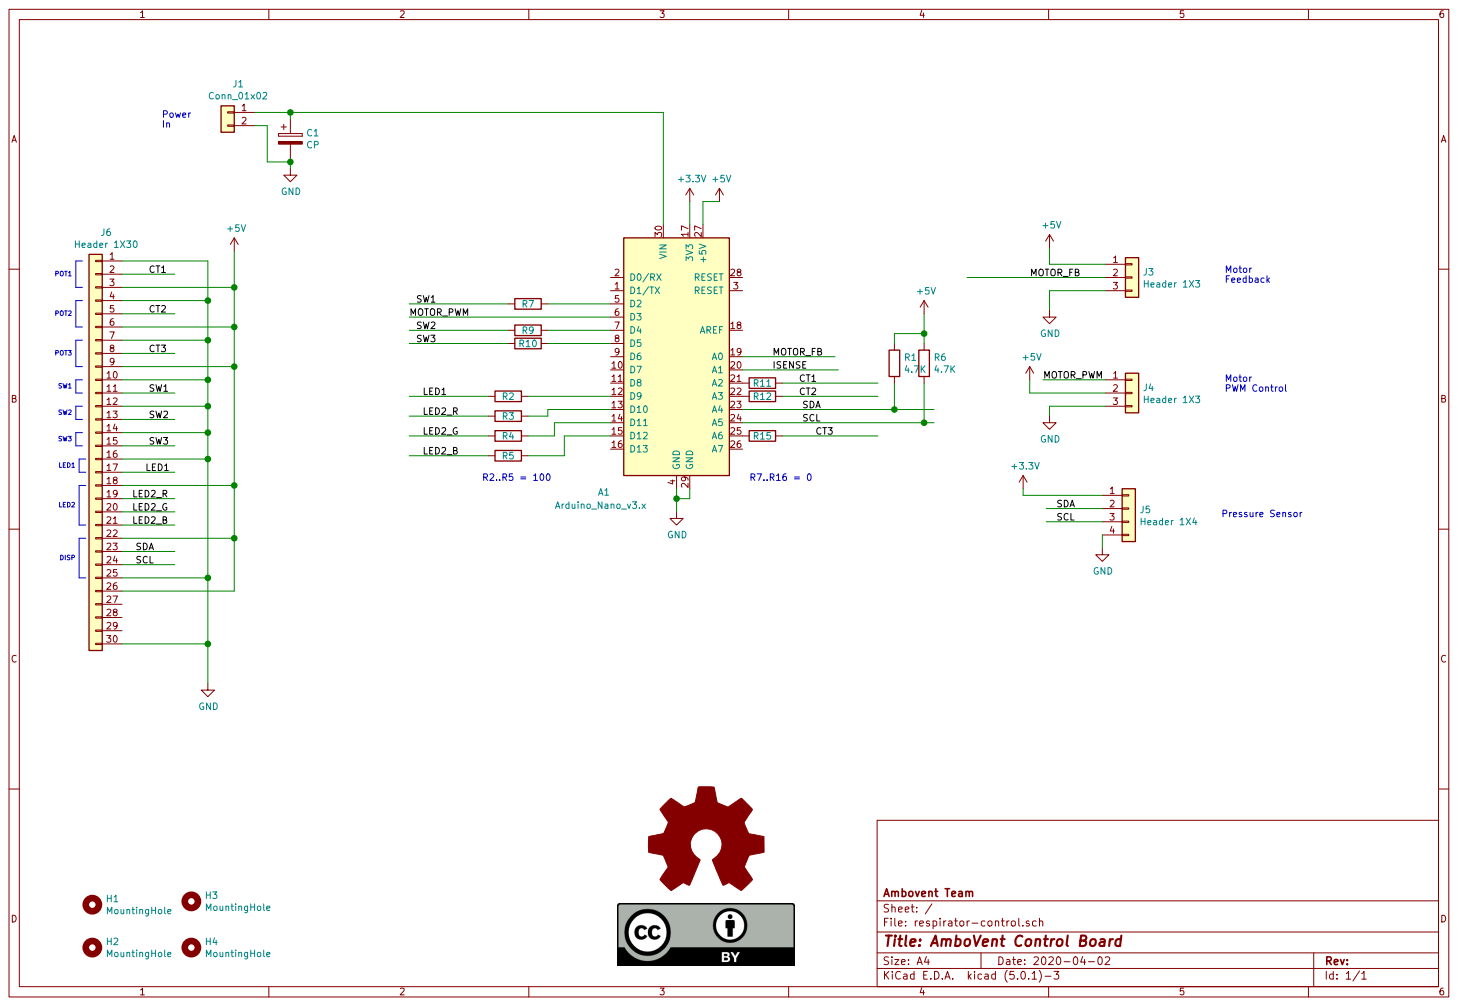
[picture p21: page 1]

19 20 LED2_G 21 LED2_B 22

23 SDA 24 25

File: respirator-control.sch Sheet: / Ambovent Team

Id: 1/1 Title: AmboVent Control Board

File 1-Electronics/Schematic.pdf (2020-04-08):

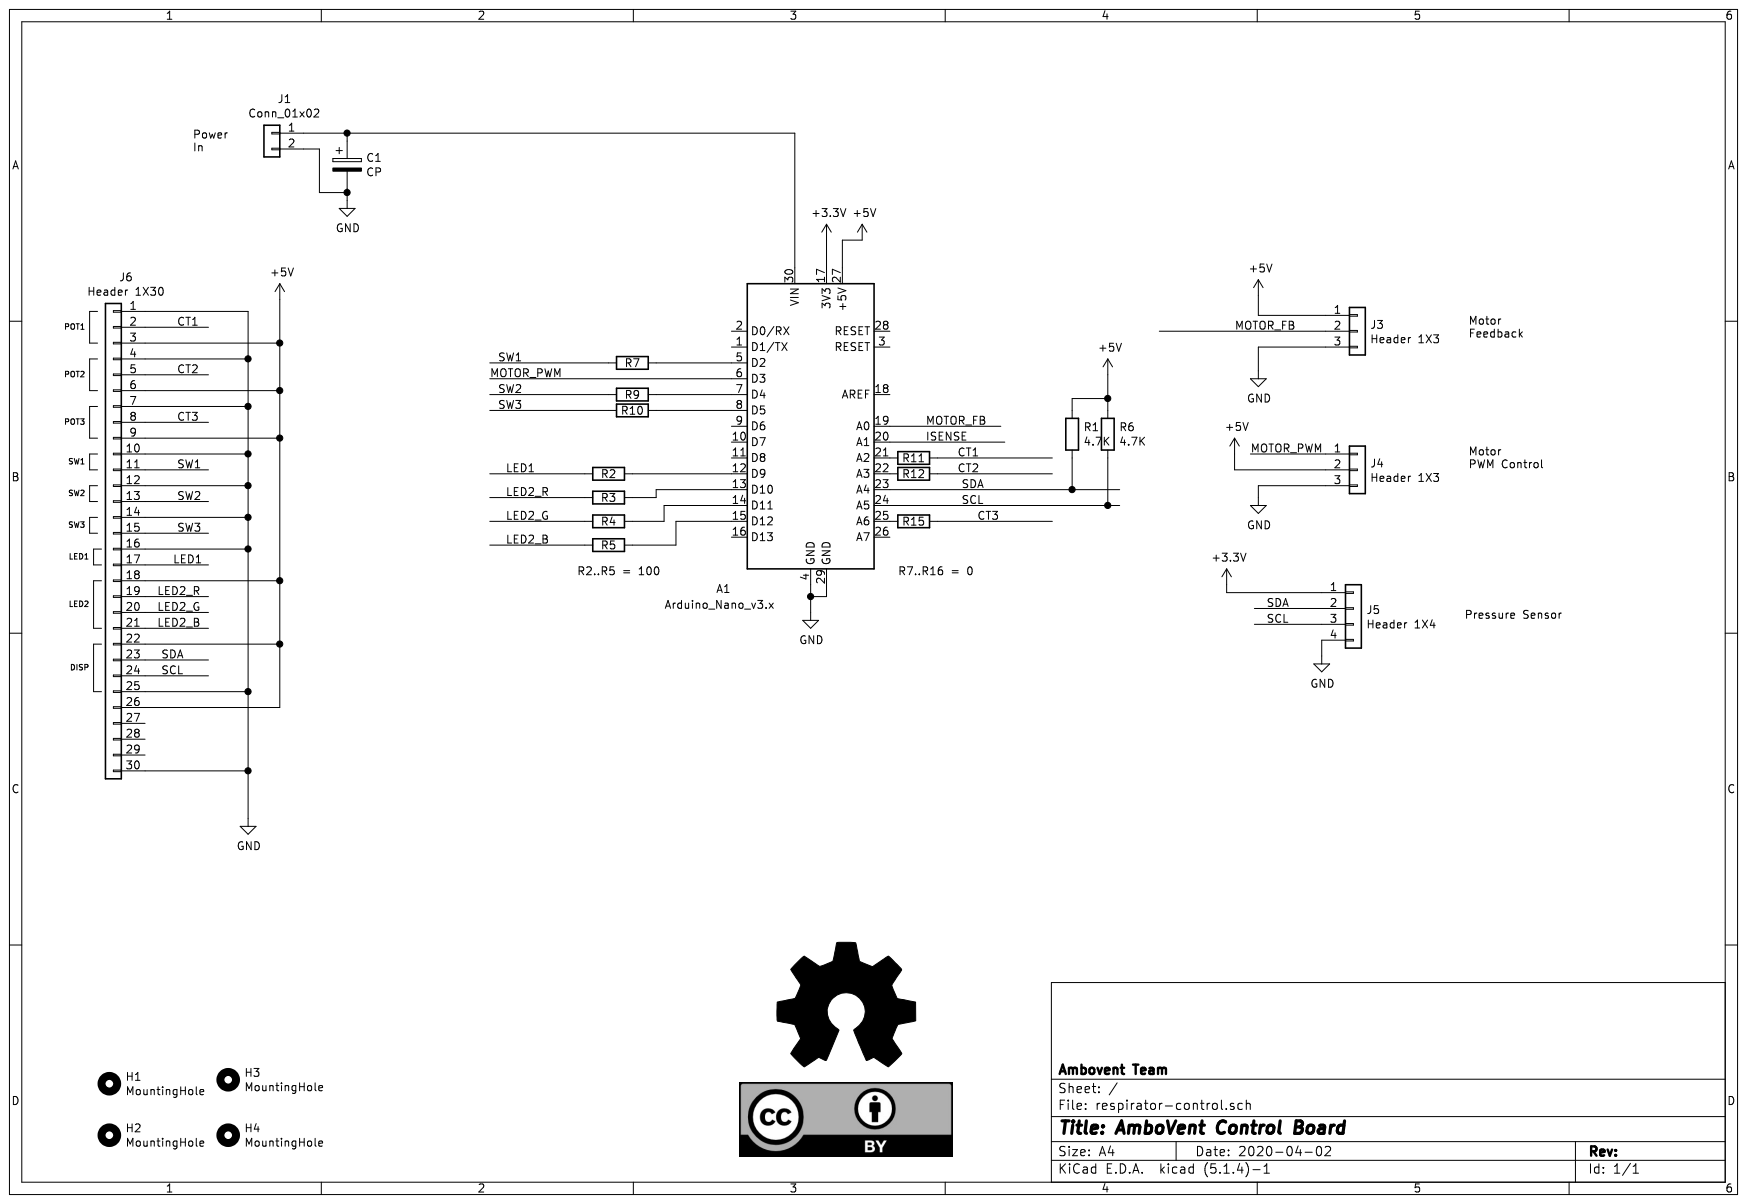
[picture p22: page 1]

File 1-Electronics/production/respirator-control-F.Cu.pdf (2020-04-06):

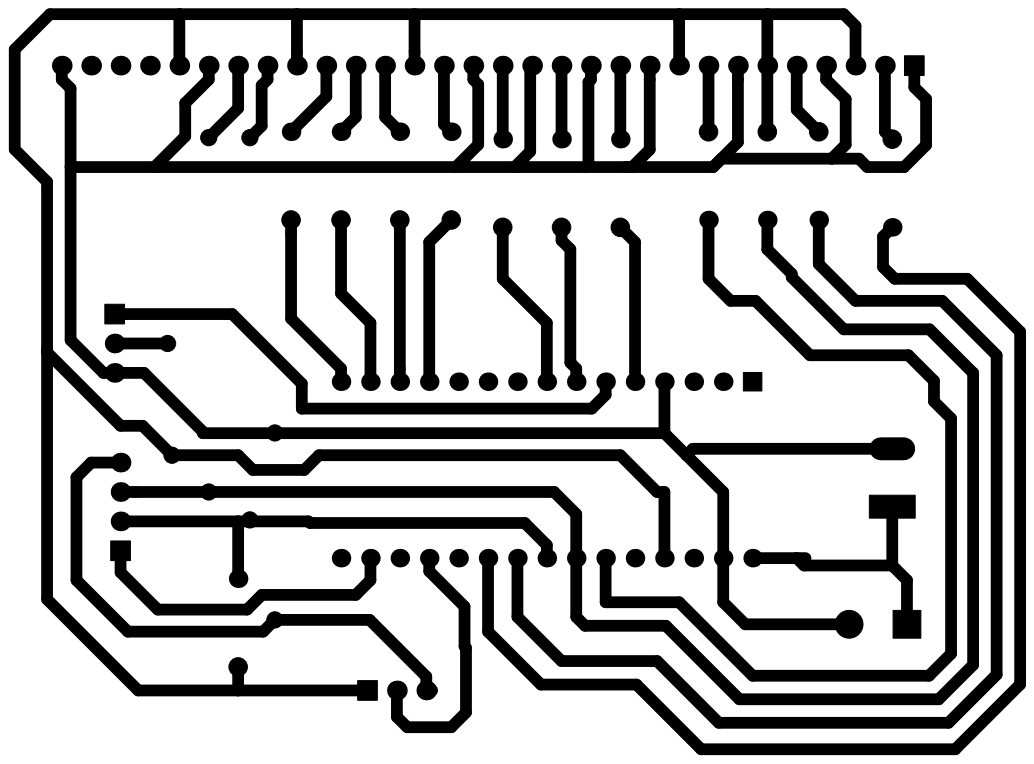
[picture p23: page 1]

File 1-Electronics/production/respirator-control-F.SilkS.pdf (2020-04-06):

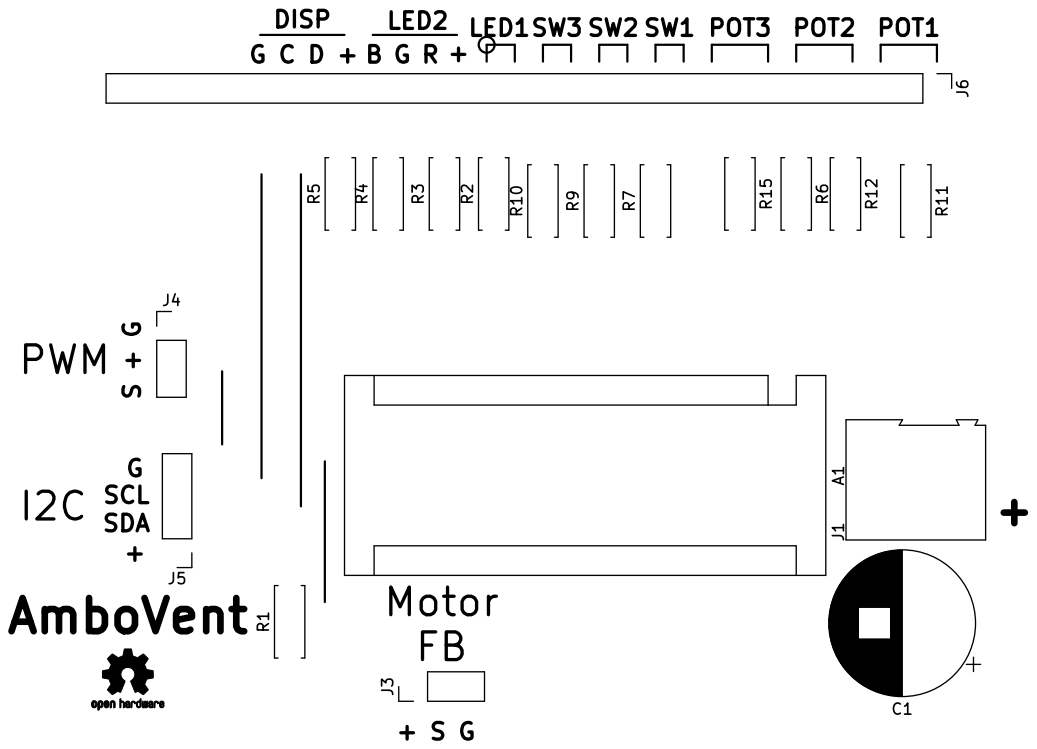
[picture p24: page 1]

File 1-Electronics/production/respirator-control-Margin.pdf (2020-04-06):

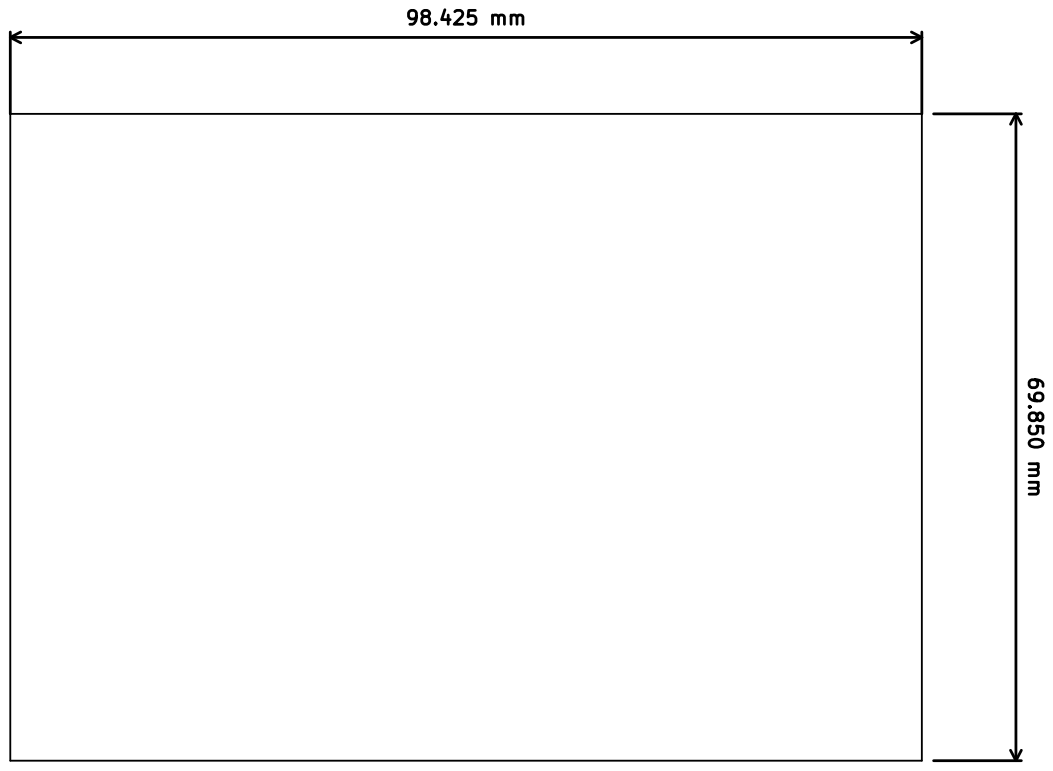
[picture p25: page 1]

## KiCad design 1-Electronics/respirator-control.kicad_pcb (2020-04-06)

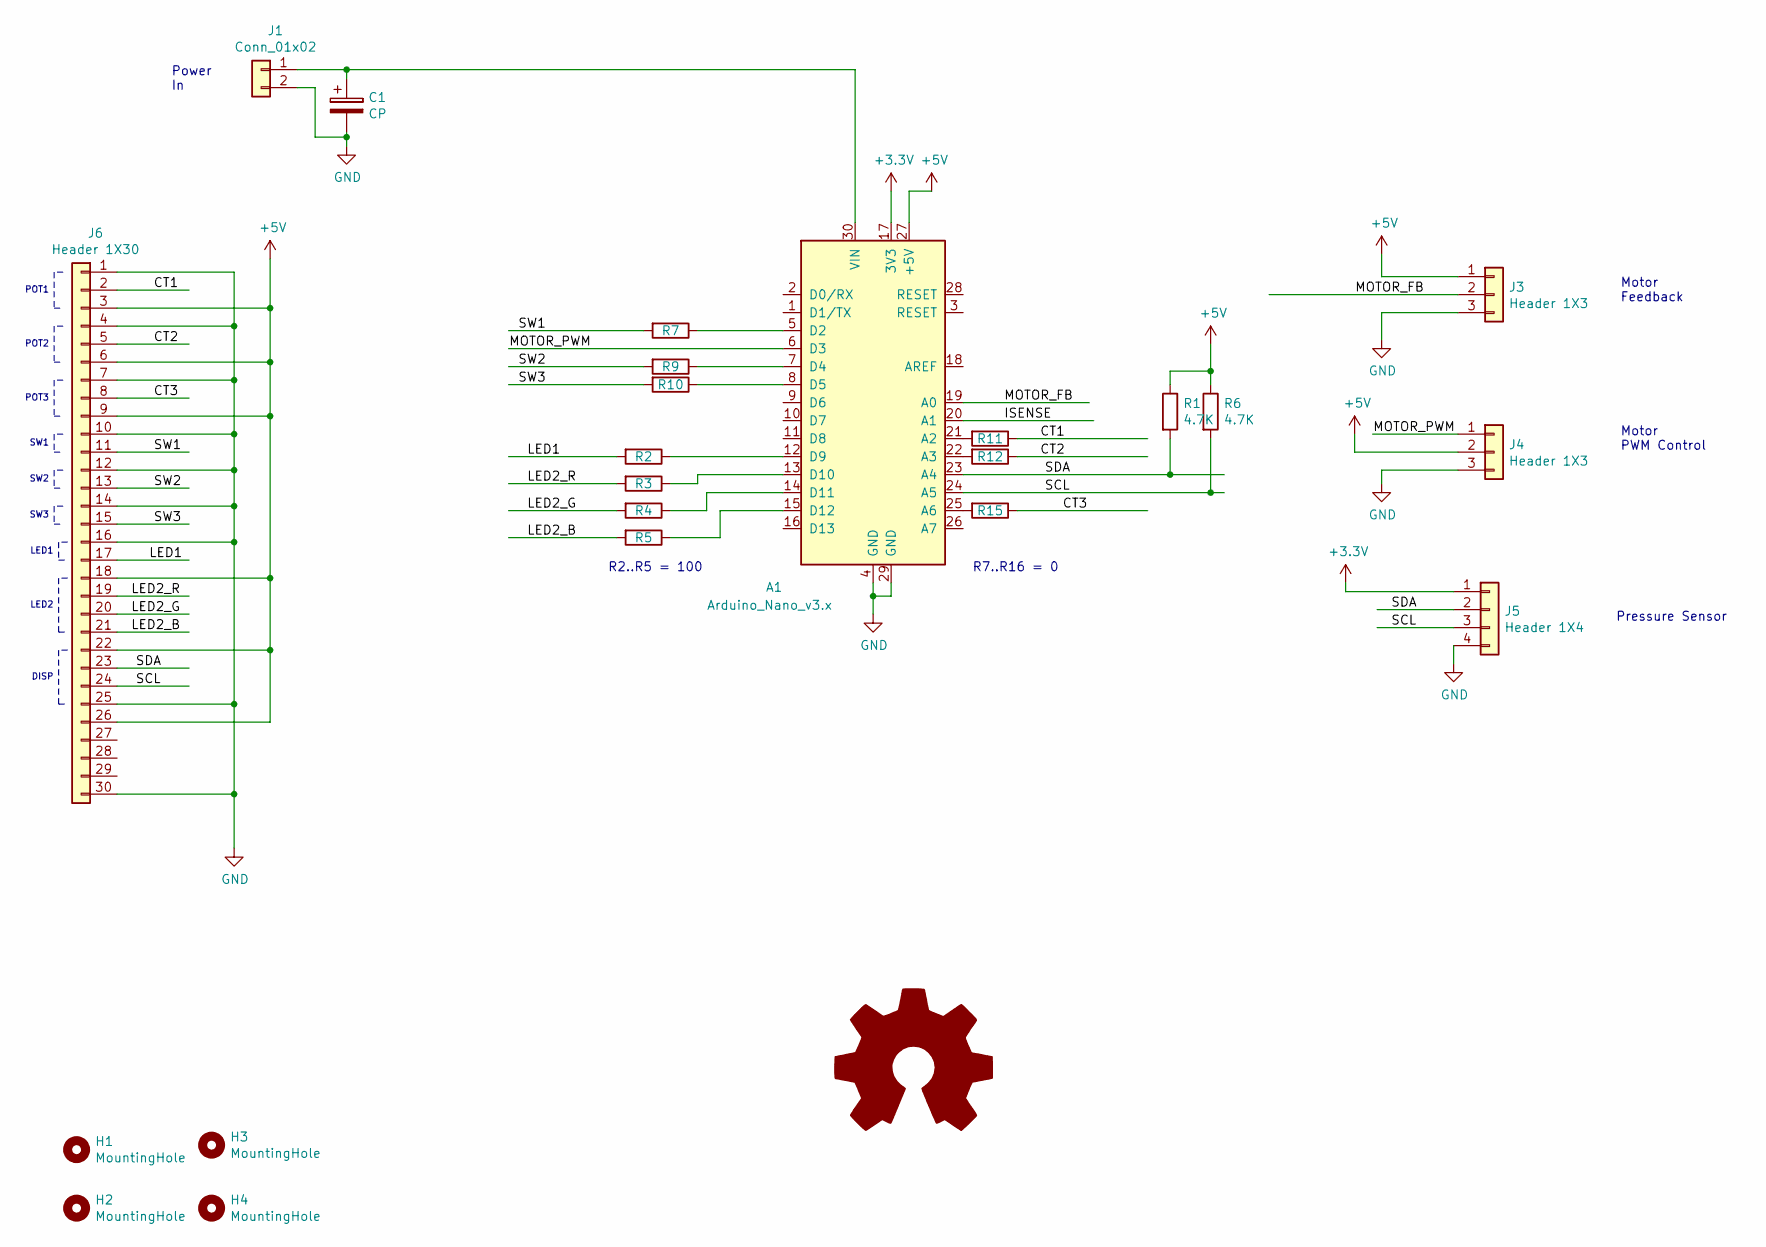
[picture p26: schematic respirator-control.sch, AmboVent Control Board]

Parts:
A1: Arduino_Nano_v3.x; Arduino_Nano
C1: CP; CP_Radial_D13.0mm_P5.00mm
H1, H2, H3, H4: MountingHole; MountingHole_3.2mm_M3
J1: Conn_01x02; TerminalBlock_Altech_AK300-2_P5.00mm
J3, J4: Header 1X3; PinHeader_1x03_P2.54mm_Vertical
J5: Header 1X4; PinHeader_1x04_P2.54mm_Vertical
J6: Header 1X30; PinHeader_1x30_P2.54mm_Vertical
R1, R6: 4.7K; R_Axial_DIN0207_L6.3mm_D2.5mm_P7.62mm_Horizontal
R2, R3, R4, R5, R7, R9, R10, R11, R12, R15: 100; R_Axial_DIN0207_L6.3mm_D2.5mm_P7.62mm_Horizontal

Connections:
+3V3: A1.17 (3V3), J5.1
+5V: A1.27 (+5V), J3.1, J4.2, J6.3, J6.6, J6.9, J6.18, J6.22, J6.26, R1.1, R6.1
/CT1: J6.2, R11.1
/CT2: J6.5, R12.1
/CT3: J6.8, R15.1
/ISENSE: A1.20 (A1)
/LED1: J6.17, R2.2
/LED2_B: J6.21, R5.2
/LED2_G: J6.20, R4.2
/LED2_R: J6.19, R3.2
/MOTOR_FB: A1.19 (A0), J3.2
/MOTOR_PWM: A1.6 (D3), J4.1
/SCL: A1.24 (A5), J5.3, J6.24, R6.2
/SDA: A1.23 (A4), J5.2, J6.23, R1.2
/SW1: J6.11, R7.2
/SW2: J6.13, R9.2
/SW3: J6.15, R10.2
GND: A1.4 (GND), A1.29 (GND), C1.2, J1.2, J3.3, J4.3, J5.4, J6.1, J6.4, J6.7, J6.10, J6.12, J6.14, J6.16, J6.25, J6.30
unnamed: A1.5 (D2), R7.1
unnamed: A1.7 (D4), R9.1
unnamed: A1.8 (D5), R10.1
unnamed: A1.12 (D9), R2.1
unnamed: A1.13 (D10), R3.1
unnamed: A1.14 (D11), R4.1
unnamed: A1.15 (D12), R5.1
unnamed: A1.21 (A2), R11.2
unnamed: A1.22 (A3), R12.2
unnamed: A1.25 (A6), R15.2
unnamed: A1.30 (VIN), C1.1, J1.1

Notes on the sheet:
Power In
R2..R5 = 100
Motor Feedback
Motor PWM Control
SW1
SW2
SW3
POT1
POT2
POT3
LED1
DISP
LED2
R7..R16 = 0
Pressure Sensor

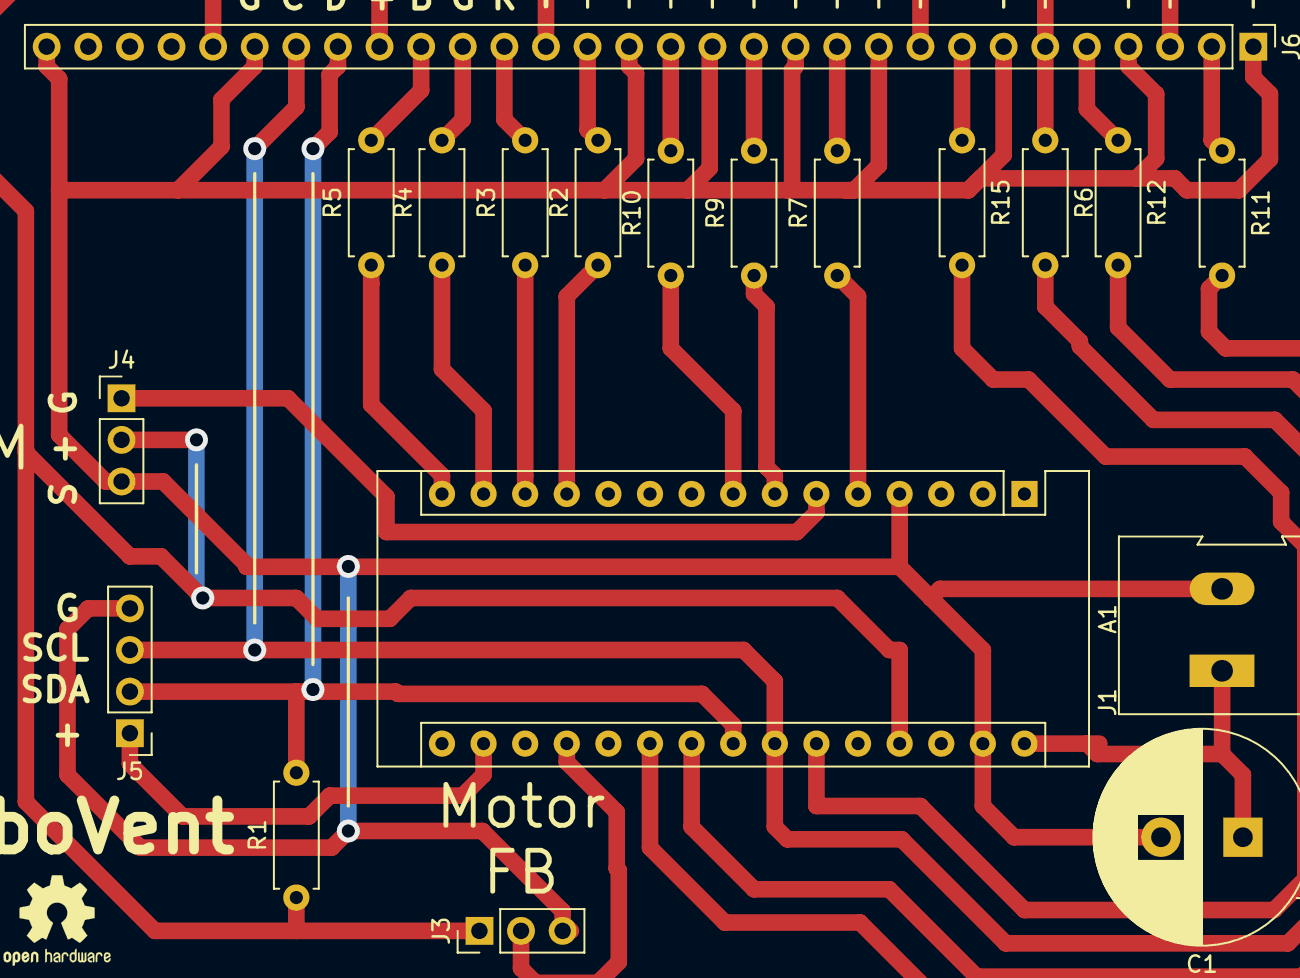
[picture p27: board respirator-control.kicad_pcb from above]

Board: 2 copper layers, 23 parts (0 on the bottom side), 28 nets.

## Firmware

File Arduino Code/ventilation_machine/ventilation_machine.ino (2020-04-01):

/*  
 *  THIS CODE WAS WRITTEN FOR USE IN A HOME MADE VENTILATION DEVICE. 
 *  IT IS NOT TESTED FOR SAFETY AND NOT RECOMENDED FOR USE IN ANY COMERCIAL DEVICE.
 *  IT IS NOT APPROVED BY ANY REGULAOTRY AUTHORITY
 *  USE ONLY AT YOUR OWN RISK 
 */
 
// system configuration 
#define full_configuration 1               //  0 if the partial system - potentiometer on pulley, no potentiometers, ...

#define pressure_sensor_available 1

// options for display and debug
#define send_to_monitor 1    // 1 = send data to monitor  0 = dont
#define telemetry 0          // 1 = send telemtry fro debug

// UI
#define deltaUD 5   // define the value chnage per each button press

// clinical 
#define perc_of_lower_volume 65.0      // % of max press - defines lower volume
#define perc_of_lower_volume_display 40.0      // % of max press - defines lower volume
#define wait_time_after_resistance 3  // seconds
#define max_pres_disconnected 10      // if the max pressure during breathing cycle does not reach this value - pipe is disconnected
#define insp_pressure_default 40      // hold this pressure while breathing 
#define safety_pres_above_insp 10     // defines safety pressure as the inspirium pressure + this one
#define safety_pressure 70            // quicly pullnack arm when reaching this
#define speed_multiplier_reverse 2    // factor of speeed for releasing the pressure (runs motion in reverse at X this speed
#define smear_factor 0                // 0 to do all cycle in 2.5 seconds and wait for the rest 1 to "smear" the motion profile on the whole cycle time 


#if (full_configuration==0)  // Arm connected with strip or wire
  #define LCD_available 0 
  #define pres_pot_available 0        // 1 if the system has 3 potentiometer and can control the inspirium pressure 
  #define pin_SW3 7   // breath - On / Off / cal
  #define pin_TST 2   // test mode - not in use
  #define pin_LED_AMP 11   // amplitude LED
  #define pin_LED_FREQ 9   // frequency LED
  #define pin_LED_Fail 10  // FAIL and calib blue LED
  #define pin_USR 12  // User LED
  #define pin_FD 4    // freq Down
  #define pin_FU 5    // freq Up
  #define pin_AD 8    // Amp Down
  #define pin_AU 6    // Amp Up
  #define curr_sense 1 
  #define control_with_pot 0    // 1 = control with potentiometers  0 = with push buttons
  
  #define F 0.6       // motion control feed forward  
  #define KP 0.2      // motion control propportional gain 
  #define KI 2        // motion control integral gain 
  #define integral_limit 6  // limits the integral of error 
  #define f_reduction_up_val 0.65   // reduce feedforward by this factor when moving up 
#endif

#if (full_configuration==1) // Direct arm conection 
  #define LCD_available 1 
  #define pres_pot_available 1        // 1 if the system has 3 potentiometer and can control the inspirium pressure 
  #define pin_SW3 4         // breath - On / Off / cal
  #define pin_TST 2         // test mode - not in use
  #define pin_RST 5         // reset alarm - not in use
  #define pin_LED_AMP 13    // amplitude LED
  #define pin_LED_FREQ 13   // frequency LED
  #define pin_LED_Fail 10   // FAIL and calib blue LED
  #define pin_USR 9         // User LED

  #define pin_FD 13    // freq Down
  #define pin_FU 13    // freq Up
  #define pin_AD 13    // Amp Down
  #define pin_AU 13    // Amp Up
  #define curr_sense 0
  #define control_with_pot 1    // 1 = control with potentiometers  0 = with push buttons

  #define F 0.6       // motion control feed forward  
  #define KP 0.2      // motion control propportional gain 
  #define KI 2        // motion control integral gain 
 
//  #define F 6       // motion control feed forward  
//  #define KP 1.6    // motion control propportional gain 
//  #define KI 0      // motion control integral gain 
  #define integral_limit 6  // limits the integral of error 
  #define f_reduction_up_val 0.65    // reduce feedforward by this factor when moving up 

#endif

// Arduino pins alocation
#define pin_PWM 3

#define pin_POT 0   // analog pin of potentiometer
#define pin_CUR 1   // analog pin of current sense
#define pin_AMP 2   // analog pin of amplitude potentiometer control
#define pin_FRQ 3   // analog pin of amplitude frequency control
#define pin_PRE 6   // analog pin of pressure control

// Talon SR controller PWM settings ("angle" for Servo library) 
#define PWM_mid 93  // mid value for PWM 0 motion - higher pushes up
#define PWM_max 85
#define PWM_min -85
#define max_allowed_current 100 // 10 Amps

// motion control parameters
#define cycleTime 5        // milisec
#define alpha 0.95         // filter for current apatation - higher = stronger low pass filter
#define profile_length 500 // motion control profile length 
#define motion_control_allowed_error  30  // % of range

// motor and sensor definitions
#define invert_mot 1
#define invert_pot 0
#define min_address 4
#define max_address 8

#include <EEPROM.h>
#include <Servo.h> 
#include <Wire.h>
#include <SparkFun_MS5803_I2C.h> 
#include <LiquidCrystal_I2C.h>
#include "ArduinoUniqueID.h"

Servo motor;
LiquidCrystal_I2C lcd(0x27, 16, 2); // Set the LCD address to 0x27 for a 16 chars and 2 line display
MS5803 sparkfumPress(ADDRESS_HIGH);

// Motion profile parameters 
// pos byte 0...255  units: promiles of full range
// vel int 0...255  ZERO is at 128 , units: pos change per 0.2 sec

// profile data:  press 250 points (50%) relase 250 

byte pos[profile_length]={0,0,0,0,1,1,1,2,2,3,3,4,5,5,6,7,8,9,10,11,12,14,15,16,17,19,20,22,23,25,27,28,30,32,33,35,37,39,41,43,45,47,49,51,53,55,57,59,62,64,66,68,71,73,75,78,80,82,85,87,90,92,95,97,100,102,105,107,110,112,115,117,120,122,125,128,130,133,135,138,140,143,145,148,150,153,155,158,160,163,165,168,170,173,175,177,180,182,184,187,189,191,193,196,198,200,202,204,206,208,210,212,214,216,218,220,222,223,225,227,228,230,232,233,235,236,238,239,240,241,243,244,245,246,247,248,249,250,250,251,252,252,253,253,254,254,254,255,255,255,255,255,255,255,255,255,255,255,255,255,255,255,255,255,255,255,255,255,255,255,255,255,255,255,255,255,255,255,255,255,255,255,255,255,255,255,255,255,255,255,255,255,255,255,255,255,255,255,255,255,255,255,255,255,255,255,255,255,255,255,255,255,255,255,255,255,255,255,255,255,255,255,255,255,255,255,255,255,255,255,255,255,255,255,255,255,255,255,255,255,255,255,255,255,255,255,255,255,255,255,255,255,255,255,255,254,254,254,254,253,253,252,252,251,250,250,249,248,248,247,246,245,244,243,242,241,239,238,237,236,234,233,232,230,229,227,225,224,222,220,219,217,215,213,211,209,207,205,203,201,199,197,195,193,191,188,186,184,182,179,177,175,172,170,167,165,163,160,158,155,153,150,148,145,143,140,138,135,133,130,128,125,123,120,118,115,113,110,108,105,103,101,98,96,94,91,89,87,85,83,80,78,76,74,72,70,68,66,65,63,61,59,58,56,54,53,51,50,48,47,46,45,43,42,41,40,39,38,37,36,35,34,33,32,31,31,30,29,28,27,26,26,25,24,23,22,22,21,20,20,19,18,18,17,16,16,15,15,14,14,13,13,12,12,11,11,10,10,9,9,9,8,8,7,7,7,6,6,6,5,5,5,5,4,4,4,4,3,3,3,3,3,3,2,2,2,2,2,2,2,1,1,1,1,1,1,1,1,1,1,1,0,0,0,0,0,0,0,0,0,0,0,0,0,0,0,0,0,0,0,0,0,0,0,0,0,0,0,0,0,0,0,0,0,0,0,0,0,0,0};
byte vel[profile_length]={129,129,130,130,131,131,132,133,133,134,135,135,136,136,137,138,138,138,139,140,140,141,141,141,142,142,143,143,144,144,145,145,145,146,146,146,147,147,147,148,148,148,149,149,149,150,150,150,150,151,151,151,151,151,152,152,152,152,152,152,153,153,153,153,153,153,153,153,153,153,153,153,153,153,153,153,153,153,153,153,153,153,153,153,153,153,153,153,153,153,152,152,152,152,152,152,151,151,151,151,151,150,150,150,150,149,149,149,148,148,148,147,147,147,146,146,146,145,145,145,144,144,143,143,142,142,141,141,141,140,140,139,138,138,138,137,136,136,135,135,134,133,133,132,131,131,130,130,129,129,128,128,128,128,128,128,128,128,128,128,128,128,128,128,128,128,128,128,128,128,128,128,128,128,128,128,128,128,128,128,128,128,128,128,128,128,128,128,128,128,128,128,128,128,128,128,128,128,128,128,128,128,128,128,128,128,128,128,128,128,128,128,128,128,128,128,128,128,128,128,128,128,128,128,128,128,128,128,128,128,128,128,128,128,128,128,128,128,128,128,128,128,128,128,128,128,128,128,128,128,128,127,127,126,126,126,125,125,124,124,123,123,122,122,121,121,120,120,120,119,118,118,118,117,117,116,116,115,115,115,114,114,113,113,113,112,112,111,111,111,110,110,109,109,109,108,108,108,107,107,107,107,106,106,106,105,105,105,105,105,104,104,104,104,104,104,103,103,103,103,103,103,103,103,103,103,103,103,103,103,103,103,103,103,103,103,104,104,104,104,104,105,105,105,105,105,106,106,106,107,107,107,108,108,108,109,109,109,110,110,111,111,112,112,113,113,114,114,114,115,116,116,116,117,117,118,118,118,118,118,119,119,119,119,119,119,119,120,120,120,120,120,120,120,121,121,121,121,121,121,121,122,122,122,122,122,122,122,123,123,123,123,123,123,123,124,124,124,124,124,124,124,124,124,125,125,125,125,125,125,125,125,125,126,126,126,126,126,126,126,126,126,126,126,126,127,127,127,127,127,127,127,127,127,127,127,127,127,127,127,127,127,127,128,128,128,128,128,128,128,128,128,128,128,128,128,128,128,128,128,128,128,128,128,128,128,128,128,128,128,128,128,128,128,128,128,128,128,128,128};

byte FD,FU,AD,AU,FDFB,FUFB,ADFB,AUFB,SW3,SW3FB,TSTFB,run_profile,LED_status,USR_status,blueOn,calibrated=0, calibON, numBlinkAmp,numBlinkFreq;
int A_pot,prevA_pot, A_current, A_amplitude=80, prev_A_amplitude, A_freq;
int motorPWM,index=0, prev_index,i, wait_cycles,cycle_number, cycles_lost,index_last_motion;
unsigned int max_arm_pos=600, min_arm_pos=500;
float wanted_pos, wanted_vel_PWM, range, range_factor, profile_planned_vel, planned_vel, integral, error, f_reduction_up ;
unsigned long lastSent,lastBlink, lastIndex, lastUSRblink,last_TST_not_pressed,lastBlue,start_wait, last_sent_data, last_read_pres,start_disp_pres;
byte monitor_index=0, BPM=14,prev_BPM, in_wait, failure, send_beep, wanted_cycle_time, disconnected=0,high_pressure_detected=0, motion_failure=0, sent_LCD, hold_breath, safety_pressure_detected;
byte counter_ON,counter_OFF,SW3temp,insp_pressure,prev_insp_pressure, safety_pressure_counter, no_fail_counter,TST, counter_TST_OFF,counter_TST_ON,TSTtemp;
float pressure_baseline;
int pressure_abs,breath_cycle_time, max_pressure=100 , prev_max_pressure=100, min_pressure=999, prev_min_pressure=999, index_to_hold_breath;

void setup() {
  pinMode (pin_PWM,OUTPUT);
  pinMode (pin_FD,INPUT_PULLUP);
  pinMode (pin_FU,INPUT_PULLUP);
  pinMode (pin_AD,INPUT_PULLUP);
  pinMode (pin_AU,INPUT_PULLUP);
  pinMode (pin_SW3,INPUT_PULLUP);
  pinMode (pin_TST,INPUT_PULLUP);
  pinMode (pin_LED_AMP,OUTPUT);
  pinMode (pin_LED_FREQ,OUTPUT);
  pinMode (pin_LED_Fail,OUTPUT);
  pinMode (pin_USR,OUTPUT);

  motor.attach(pin_PWM); 
  Serial.begin (115200);
  Wire.begin();
  
  if (pressure_sensor_available) {
  sparkfumPress.reset();
  sparkfumPress.begin();
  pressure_baseline = sparkfumPress.getPressure(ADC_4096);
  }
  
  if (LCD_available){
    lcd.begin();  // initialize the LCD
    lcd.backlight();  // Turn on the blacklight and print a message.
  }
  
  for (i = 0; i < 2; i++) {UniqueIDdump(Serial);  delay(100); }
  
  run_profile=0;
  EEPROM.get(min_address, min_arm_pos);   delay (100);
  EEPROM.get(max_address, max_arm_pos);  delay (100);
  if (min_arm_pos>=0 && min_arm_pos<1024 && max_arm_pos>=0 && max_arm_pos<1024) calibrated = 1;
  insp_pressure=insp_pressure_default;
}

void loop() 
{
  read_IO ();
  run_profile_func ();
  find_min_max_pressure();
  if (LCD_available) {if (index >= (profile_length-2)) 
                      if (sent_LCD==0) {sent_LCD=1; display_LCD();}
                      if (index==0) sent_LCD=0;
                      }

  if (millis()-last_sent_data>7)
  { 
      if (telemetry) print_tele();
      if (send_to_monitor) send_data_to_monitor();
      last_sent_data=millis();
  }

  if (TST==0) last_TST_not_pressed=millis();
  if (millis()-last_TST_not_pressed>5000) calibrate_range();
  if (calibrated ==0) { run_profile=0;  calibrate_range(); }
}
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

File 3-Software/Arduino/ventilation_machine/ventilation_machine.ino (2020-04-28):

/*
THIS CODE WAS WRITTEN FOR TESTING AND RUNNING A HOME-MADE VENTILATION DEVICE.
IT IS NOT TESTED FOR SAFETY AND NOT APPROVED FOR USE IN ANY CLINICAL, MEDICAL OR COMERCIAL DEVICE.
IT IS NOT APPROVED BY ANY REGULATORY AUTHORITY.
USE ONLY AT YOUR OWN RISK.

To start calibrations:
First enter the maintenance setup menu by pressing the TEST button for 3 seconds.
Using the RATE potentiometer select the calibration required and press TEST to select.
Follow instructions on the screen.

For the Arm range calibration:
Use the Rate potentiometer to move the arm up/down.
*/

#include <EEPROM.h>
#include <LiquidCrystal_I2C.h>
#include <Servo.h>
#include <SparkFun_MS5803_I2C.h>
#include <Wire.h>
#include "ArduinoUniqueID.h"

/// Version string: be sure to update this version number EVERY time you make any code change,
/// period, which isn't just a comment change! Document it in the Software Changelog in the main
/// AmboVent readme.
#define VERSION_STR "v0.1.0"

// TODO(ElectricRCAircraftGuy): get rid of nearly every single one of these #defines! They should
// be `constexpr` variables instead, with the sole exception of ones which are used for variable
// compilation, such as those which exclude certain portions of code based on hardware
// configuration. (Even this may not be true though, as using bool may still allow the compiler
// to optimize out those sections. Do some compilation testing when you get to it).

// System Configuration

/// Set to true for "full system" (the default), or to false for "partial system"--potentiometer
/// installed on pulley, no potentiometers... <---? TODO(@ElectricRCAircraftGuy): I request further
/// explanation from @nimrod46--please update this description to be more clear.
#define FULL_CONFIGURATION true
/// Set to true if you have installed an I2C pressure sensor
#define PRESSURE_SENSOR_AVAILABLE true
/// Set to true to send unique ID for 10 seconds at startup, false otherwise
#define CENTRAL_MONITOR_SYSTEM false

// Options for display and debug via serial communication port

/// Set to true to send data to the Serial Monitor, false otherwise
#define SEND_TO_MONITOR true
/// Set to true to send telemetry for debugging, false otherwise. See the end of this file for the
/// optional telemetry data to send (comment/uncomment selected lines as desired)
#define TELEMETRY false

// User Interface (UI) settings

/// Define the value change per button press, in percent, for the non-potentiometer version only
#define DELTA_COMPRESSION_PERCENT 5
/// IIR (Infinite Impulse Response) low-pass filter constant to filter the potentiometer values.
/// This is a floating point value that must be >= 0 and < 1.0. Make closer to 1.0 to increase
/// the strength of the low-pass filter, lowering the cutoff frequency and reducing the frequency
/// response, and closer to 0 to have the opposite effect.
#define POT_ALPHA 0.85

// Clinical settings
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

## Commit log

2020-03-31 Giora's changes:
    Add disclaimer.
    Added Command and Control setup
    Added test button - still not in use
    Fix pres_pot range
    Moved clinical const up.
    Fix pin_USR LED for config 1.
    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
2020-03-31 Moved code to it's folder so it could be open in arduino's IDE
2020-04-01 first commit - mechanisms design
    [0.5in Hex 1.125in OD 217-3875 Flanged Bearing.SLDPRT, 1690-20-8300 REV7 26.3.2020 20_30.STEP, 1690-20-8300 REV7 26.3.2020 20_30.x_t, 1690-20-8300 Geometry.SLDP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]
2020-04-02 added footage
    [1.STL, 2.STL, PResure sensor Box.x_t]
2020-04-02 added pot calibration and fail messages
2020-04-02 added filters to pot (for shoham :-) )
2020-04-02 added motor definition and comments to SW code
2020-04-02 Removed url files, organized folders
    [0.5in Hex 1.125in OD 217-3875 Flanged Bearing.SLDPRT, 1.STL, 1690-20-8300 REV7 26.3.2020 20_30.STEP, 1690-20-8300 REV7 26.3.2020 20_30.x_t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]
2020-04-02 Prioritized folders order
    [0.5in Hex 1.125in OD 217-3875 Flanged Bearing.SLDPRT, 1.STL, 1690-20-8300 REV7 26.3.2020 20_30.STEP, 1690-20-8300 REV7 26.3.2020 20_30.x_t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]
2020-04-03 Order in mechanism folder
    [0.5in Hex 1.125in OD 217-3875 Flanged Bearing.SLDPRT, 1690-20-8300 REV7 26.3.2020 20_30.STEP, 1690-20-8300 REV7 26.3.2020 20_30.x_t, 1690-20-8300 Geometry.SLDP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]
2020-04-03 Upload the most updated schematic + PCB
    [respirator-control-F.Cu.gbr, respirator-control-F.SilkS.gbr, respirator-control-Margin.gbr, respirator-control.drl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]
2020-04-04 added calibration video
2020-04-04 Added images and fixed names in pressure sensor folder
    [Box.STL, Cover.STL, Pressure sensor Box.x_t]
2020-04-04 Moved presser sensor to its own folder and add some more files to it
    [Box.STL, Cover.STL, Pressure sensor Box.x_t]
2020-04-06 Added x_t parts files to mechanics
    [1690-20-8300.x_t, 1690-20-8311.x_t, 1690-20-8313.x_t, 1690-20-8321.x_t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]
2020-04-06 added Arduino libs
2020-04-06 moved the calibration video to BU folder - not updated
2020-04-07 Added drawings to mechanics
    [1690-20-8300.SLDDRW, 1690-20-8320.SLDDRW, 1690-20-8340.SLDDRW, 1690-20-8390.SLDDRW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]
2020-04-12 Rename folders to make them not hidden; add Linux URL to YouTube demo video; update readme
    Files and folders that begin with a period (.) on Linux and Mac are
    hidden, so I have renamed the following folders to make them not hidden
    anymore, while still keeping them near the top of the alphabetical
    order, which seemed to be intentional, and keeping them in the same
    order:
    1. .Electronics --> 1-Electronics
    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
    [0.5in Hex 1.125in OD 217-3875 Flanged Bearing.SLDPRT, 1690-20-8300 REV7 26.3.2020 20_30.STEP, 1690-20-8300 REV7 26.3.2020 20_30.x_t, 1690-20-8300 Geometry.SLDP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]
2020-04-12 Add arduino_core folder & "3-Software/Arduino/arduino_core/readme.md" readme
2020-04-12 Add 3-Software/Arduino/arduino_core/readme.md & .gitignore file
2020-04-12 Add Eclipse project to index and be able to explorer all Arduino source code
    This includes the AmboVent .ino file as well as ALL Arduino core source
    code as well!
2020-04-14 .clang-format: changed tab size from 2 --> 4 & added detailed info about getting a good editor
    I explained how to set tab size in Arduino IDE from 2 to 4, but also
    recommended just getting a good editor, and setting the IDE to "Use
    external editor", so you just build with it, but no longer edit with it.
    Good editor examples & descriptions
    (I added detailed descriptions for these editors):
    1. Eclipse
    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
2020-04-21 I opened the Eclipse project on a new computer which caused a hash change in "3-Software/Arduino/.settings/language.settings.xml"
    If this becomes problematic, causing a hash change for anyone who opens
    this file in Eclipse, we'll have to add this file to the .gitignore
    list. Sharing Eclipse configuration files in version control is still
    a bit new to me.
2020-04-21 Clean up the top section of #defines; change all `byte` types to `uint8_t`
    Cleaning up the #defines included:
    1. renaming to have more descriptive names, names in ALL_CAPITALS, and
    names which ended in their units (ex: _PA for Pascals)
    2. Changing all 0s meaning false to `false`, all 1s meaning true to
    `true`
    3. Adding more detailed descriptions, such as for the low-pass-filter
    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
2020-04-21 Update ventilation_machine/readme.md to show it still builds in Arduino w/virtually no binary size changes
2020-04-21 Added drawings to specific parts
    [1690-20-8311.SLDDRW, 1690-20-8321.SLDDRW, 1690-20-8325.SLDDRW, 1690-20-8391.SLDDRW]
2020-04-26 Calibrated ambovent PID
2020-04-28 Added RGB led, moved motion_failure check to calc_failure func
    Runned code formatting with "./run_clang-format.sh"
